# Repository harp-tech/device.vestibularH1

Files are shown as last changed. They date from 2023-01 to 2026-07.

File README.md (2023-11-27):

## Harp VestibularH1

This repository contains the device metadata, firmware and high-level interface to the VestibularH1 device. Below are simple getting started instructions for maintainers to create a new device using the automatic code generators.

### Device metadata

#### Prerequisites

1. Install [Visual Studio Code](https://code.visualstudio.com/)
2. Install the [YAML](https://marketplace.visualstudio.com/items?itemName=redhat.vscode-yaml) extension.

The `device.yml` file in the root of the project contains the VestibularH1 device metadata. A complete specification of device registers, including any bit masks, group masks, and payload specs needs to be provided for code generation to work.

### Generating interface and firmware

#### Prerequisites

1. Install [`dotnet`](https://dotnet.microsoft.com/)
2. Install `dotnet-t4`
```
dotnet tool install -g dotnet-t4
```

The `Generators` folder contains all text templates and project files required to generate both the firmware headers and the interface for the VestibularH1 device. To run the text templating engine just build the project inside this folder.

```
cd Generators
dotnet build
```

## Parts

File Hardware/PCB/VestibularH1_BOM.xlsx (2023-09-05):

VestibularVR H1-module v.1.1 BOM
Qty | Parts | Value | OEPS | MPN | Device | Package | Description
2 | R1, R5 | 0R | OEPS020001 | RC0402JR-070RL | R-US_R0402 | R0402@1 | RESISTOR, American symbol
14 | C3, C5, C7, C9, C12, C14, C15, C16, C17, C25, C26, C27, C28, C29 | 100nF | OEPS010004 | C1005X7R1H104K050BB | C-EUC0402K | C0402K | CAPACITOR, European symbol
4 | R4, R7, R18, R34 | 10k | OEPS020030 | CRCW040210K0FKED | R-US_R0402 | R0402@1 | RESISTOR, American symbol
3 | R3, R8, R9 | 1M | OEPS020026 | CRCW04021M00FKED | R-US_R0402 | R0402@1 | RESISTOR, American symbol
2 | LICK_0, LICK_1 | 1x3 case | OEPS070035 | 282834-3 | 22-23-2031 | 22-23-2031 | .100 (2.54mm) Center Header - 3 Pin"
2 | CAM_TRIGGERS, REWARD_VALVES | 1x4 case | OEPS070036 | 282834-4 | 22-23-2041 | 22-23-2041 | .100 (2.54mm) Center Header - 4 Pin"
2 | X1, X2 | 2x5 header | n.a. | 2x5 header | TSW-105-02-S-D | TSW-105-02-S-D | THROUGH-HOLE .025 SQ POST HEADER"
1 | R10 | 330R | OEPS020037 | RC0402FR-07330RL | R-EU_R0402 | R0402 | RESISTOR, European symbol
1 | C2 | 4.7nF | OEPS010001 | CC0402KRX7R8BB472 | C-EUC0402K | C0402K | CAPACITOR, European symbol
3 | C8, C10, C11 | 4.7uF | OEPS010018 | C1608X6S1C475K080AC | C-EUC0603 | C0603 | CAPACITOR, European symbol
2 | L1, L2 | 40R@100MHz | OEPS040003 | MI0805K400R-10 | R-EU_R0603 | R0603 | RESISTOR, European symbol
3 | C4, C6, C13 | 47pF | n.a. | 04025A470JAT2A | C-EUC0402K | C0402K | CAPACITOR, European symbol
1 | IC8 | ATXMEGA32A4U | OEPS080012 | ATXMEGA32A4U-AUR | XMEGA-A4_AT-XMEGA-XXA4-AUTQFP44 | TQFP44 | ATxMega a4 Serie
2 | D1, D4 | BAT54 | OEPS030003 | BAT54SLT1G | BAT54 | SOT23 | Schottky Diodes
2 | T1, T2 | DMG1012UW | OEPS060010 | DMG1012UW-7 | DMG1012UW-7 | SOT323 | N-CHANNEL ENHANCEMENT MODE MOSFET
2 | R2, R6 | DNI | DNI | DNI | R-US_R0402 | R0402@1 | RESISTOR, American symbol
1 | IC1 | FT232RL | OEPS080013 | FT232RL | FT232RL | SSOP28 | UART/FIFO IC
1 | STATE | GREEN_LED | OEPS030005 | LTST-C191KGKT | LEDCHIP-LED0603 | CHIP-LED0603 | LED
1 | IC3 | LP5907MFX-3.3 | OEPS080016 | LP5907MFX-3.3/NOPB | TLV700XX | TSOT23-5 | C REG LINEAR 3.3V 200MA SOT23-5
4 | IC2, IC4, IC5, IC9 | M74VHC1GT126DT1G | OEPS080017 | M74VHC1GT126DT1G | M74VHC1GT126DT1G | TSOP-5 | Single Buffer/Driver With Open-Drain Output
1 | X15 | Main_plug | OEPS070037 | 20.155MH/5-E | 90G-5 | 90G-5 | WEIDMUELLER CLAMP CONNECTOR
1 | OSC1 | OSCILLATOR | OEPS080018 | DSC1001CI5-032.0000 | OSCILLATOR | OSCILLATOR_3.2X2.5 | XTAL OSC TCXO 32.0000MHZ HCMOS
1 | SV2 | PINHD-2X3 | OEPS070015 | 609-3210-ND | PINHD-2X3 | 2X03 | PIN HEADER
1 | X3 | USB_MINI_B | OEPS070021 | UX60-MB-5S8 | USB_MINI_B | 240-0002-1 | CONN RCPT USB2.0 MINI B SMD R/A
1 | IC7 | USBLC6-2SC6 | OEPS030010 | USBLC6-2SC6 | USBLC6-2SC6 | SOT23-6L | TVS DIODE 5.25VWM 17VC SOT23-6
.off board
Qty | Value | Parts | OEPS | Device | MPN | Package | Description
1 | CONN RCPT 10POS IDC 28AWG | n.a. | OEPS070040 | - | 1658621-1 AKC10H-ND | 2x5 10mil pitch | IDC 2x5 10mil pitch
1 | PAA5100JE Near Optical Flow Camera SPI Breakout | n.a. | OEPS ?? | - | PAA5100JE | - | PAA5100JE-Q is PixArt Imaging's latest optical navigation chip
2 | Lick Sensor module v1.0 PCB | n.a. | OEPS ?? | - | Lick Sensor module v1.0 | - | Lick Sensor
1 | Pluggable Terminal Block, 3.5 mm, 5 Ways | n.a. | OEPS070038 | - | 20.1550M/5-E Farnell 2575218 | - | External Terminal Block
n | flat ribbon cable | n.a. | OEPS090003 | - | 3365/10-100SF | - | RIBON 10COND 28AWG GRAY 100FT 30.48metter

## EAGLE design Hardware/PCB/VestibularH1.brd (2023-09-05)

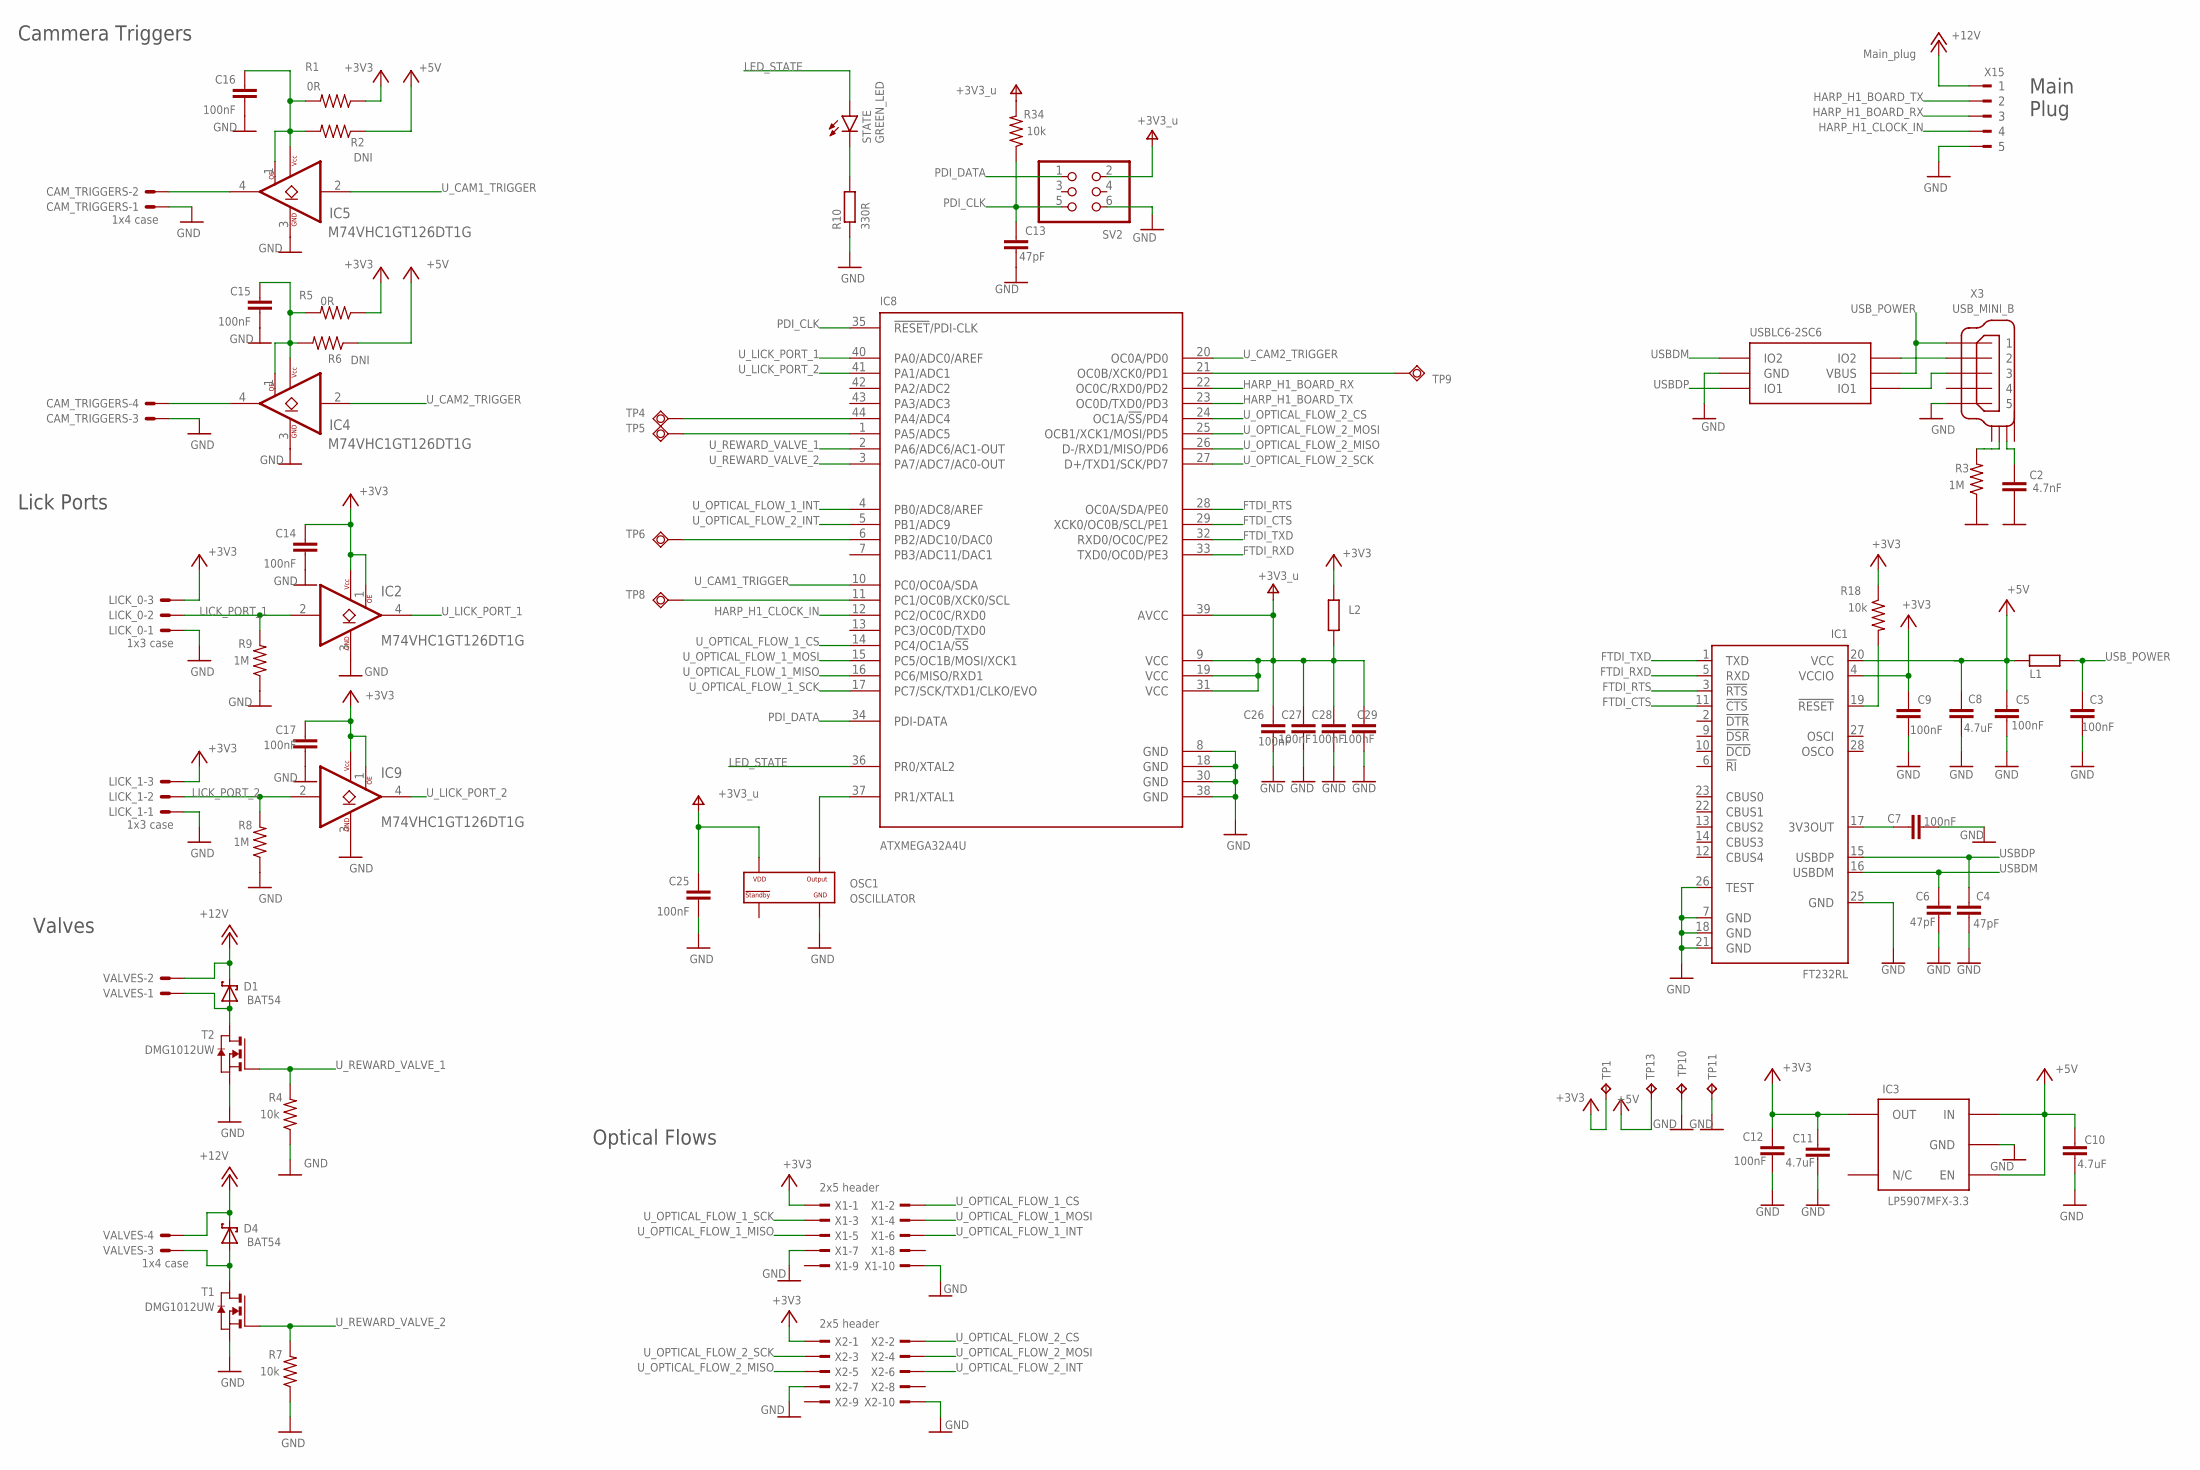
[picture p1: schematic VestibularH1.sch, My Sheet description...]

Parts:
C2: 4.7nF; C0402K; MPN CC0402KRX7R8BB472
C3, C5, C7, C9, C12, C14, C15, C16, C17, C25, C26, C27, C28, C29: 100nF; C0402K; MPN C1005X7R1H104K050BB; DIGIKEY_PN 445-5932-1-ND
C4, C6, C13: 47pF; C0402K; MPN 04025A470JAT2A
C8, C10: 4.7uF; C0603; MPN C1608X6S1C475K080AC
C11: 4.7uF; C0603K; MPN C1608X6S1C475K080AC
CAM_TRIGGERS: 1x4 case; 22-23-2041; MPN 282834-4
D1, D4: BAT54; SOT23; MPN BAT54SLT1G
IC1: FT232RL; SSOP28; MPN FT232RL
IC2, IC4, IC5, IC9: M74VHC1GT126DT1G; TSOP-5; MPN M74VHC1GT126DT1G; DIGIKEY_PN M74VHC1GT126DT1GOSDKR-ND
IC3: LP5907MFX-3.3; TSOT23-5; MPN LP5907MFX-3.3/NOPB
IC7: USBLC6-2SC6; SOT23-6L; MPN USBLC6-2SC6
IC8: ATXMEGA32A4U; TQFP44
L1, L2: 40R@100MHz; R0603; MPN MI0805K400R-10
LICK_0, LICK_1: 1x3 case; 22-23-2031; MPN 282834-3
OSC1: OSCILLATOR; OSCILLATOR_3.2X2.5; MPN DSC1001CI5-032.0000
R1, R5: 0R; R0402@1; MPN RC0402JR-070RL
R2, R6: DNI; R0402@1; MPN DNI
R3, R8, R9: 1M; R0402@1; MPN CRCW04021M00FKED; DIGIKEY_PN 541-1.00MLCT-ND
R4, R7, R18, R34: 10k; R0402@1; MPN CRCW040210K0FKED; DIGIKEY_PN 541-10.0KLDKR-ND
R10: 330R; R0402; MPN RC0402FR-07330RL
STATE: GREEN_LED; CHIP-LED0603; MPN LTST-C191KGKT
SV2: PINHD-2X3; 2X03; MPN 609-3210-ND
T1, T2: DMG1012UW; SOT323; MPN DMG1012UW-7
TP1, TP10, TP11, TP13: NO_COMPONENT; B1,27
TP4, TP5, TP6, TP8, TP9: NO_COMPONENT; TP11R
VALVES: 1x4 case; 22-23-2041; MPN 282834-4
X1, X2: 2x5 header; TSW-105-02-S-D; MPN 2x5 header
X3: USB_MINI_B; 240-0002-1; MPN UX60-MB-5S8
X15: Main_plug; 90G-5; MPN 20.155MH/5-E

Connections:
+3V3: C9.1, C11.1, C12.1, C14.1, C17.1, IC1.4 (VCCIO), IC2.1 (OE), IC2.5 (VCC), IC3.5 (OUT), IC9.1 (OE), IC9.5 (VCC), L2.2, LICK_0.3, LICK_1.3, R1.1, R5.1, R18.1, TP1.TP, X1.1, X2.1
+3V3_U: C25.1, C26.1, C27.1, C28.1, C29.1, IC8.9 (VCC), IC8.19 (VCC), IC8.31 (VCC), IC8.39 (AVCC), L2.1, OSC1.P$4 (VDD), R34.2, SV2.2
+5V: C5.1, C8.1, C10.1, IC1.20 (VCC), IC3.1 (IN), IC3.3 (EN), L1.1, R2.1, R6.1, TP13.TP
+12V: D1.3 (C), D4.3 (C), VALVES.2, VALVES.4, X15.1
FTDI_CTS: IC1.11 (!CTS), IC8.29 (XCK0/OC0B/SCL/PE1)
FTDI_RTS: IC1.3 (!RTS), IC8.28 (OC0A/SDA/PE0)
FTDI_RXD: IC1.5 (RXD), IC8.33 (TXD0/OC0D/PE3)
FTDI_TXD: IC1.1 (TXD), IC8.32 (RXD0/OC0C/PE2)
GND: C2.2, C3.2, C4.2, C5.2, C6.2, C7.2, C8.2, C9.2, C10.2, C11.2, C12.2, C13.2, C14.2, C15.2, C16.2, C17.2, C25.2, C26.2, C27.2, C28.2, C29.2, CAM_TRIGGERS.1, CAM_TRIGGERS.3, IC1.7 (GND), IC1.18 (GND), IC1.21 (GND), IC1.25 (GND), IC1.26 (TEST), IC2.3 (GND), IC3.2 (GND), IC4.3 (GND), IC5.3 (GND), IC7.P$2 (GND), IC8.8 (GND), IC8.18 (GND), IC8.30 (GND), IC8.38 (GND), IC9.3 (GND), LICK_0.1, LICK_1.1, OSC1.P$2 (GND), R3.1, R4.1, R7.1, R8.1, R9.1, R10.1, SV2.6, T1.2 (S), T2.2 (S), TP10.TP, TP11.TP, X1.7, X1.10, X2.7, X2.10, X3.P$5 (5), X15.5
HARP_H1_BOARD_RX: IC8.22 (OC0C/RXD0/PD2), X15.3
HARP_H1_BOARD_TX: IC8.23 (OC0D/TXD0/PD3), X15.2
HARP_H1_CLOCK_IN: IC8.12 (PC2/OC0C/RXD0), X15.4
LED_STATE: IC8.36 (PR0/XTAL2), STATE.A
LICK_PORT_1: IC2.2 (A), LICK_0.2, R9.2
LICK_PORT_2: IC9.2 (A), LICK_1.2, R8.2
unnamed: R3.2, X3.SHIELD_2
unnamed: IC7.P$4 (IO2), X3.P$2 (2)
unnamed: IC7.P$6 (IO1), X3.P$3 (3)
unnamed: CAM_TRIGGERS.4, IC4.4 (Y)
unnamed: C16.1, IC5.1 (OE), IC5.5 (VCC), R1.2, R2.2
unnamed: D4.1 (A), T1.3 (D), VALVES.3
unnamed: CAM_TRIGGERS.2, IC5.4 (Y)
unnamed: R10.2, STATE.C
unnamed: IC8.44 (PA4/ADC4), TP4.TP
unnamed: IC8.1 (PA5/ADC5), TP5.TP
unnamed: IC8.6 (PB2/ADC10/DAC0), TP6.TP
unnamed: C15.1, IC4.1 (OE), IC4.5 (VCC), R5.2, R6.2
unnamed: C2.1, X3.SHIELD_3
unnamed: IC8.11 (PC1/OC0B/XCK0/SCL), TP8.TP
unnamed: IC8.21 (OC0B/XCK0/PD1), TP9.TP
unnamed: C7.1, IC1.17 (3V3OUT)
unnamed: D1.1 (A), T2.3 (D), VALVES.1
unnamed: IC1.19 (!RESET), R18.2
OSC2: IC8.37 (PR1/XTAL1), OSC1.P$3 (OUTPUT)
PDI_CLK: C13.1, IC8.35 (!RESET!/PDI-CLK), R34.1, SV2.5
PDI_DATA: IC8.34 (PDI-DATA), SV2.1
USBDM: C6.1, IC1.16 (USBDM), IC7.P$3 (IO2)
USBDP: C4.1, IC1.15 (USBDP), IC7.P$1 (IO1)
USB_POWER: C3.1, IC7.P$5 (VBUS), L1.2, X3.P$1 (1)
U_CAM1_TRIGGER: IC5.2 (A), IC8.10 (PC0/OC0A/SDA)
U_CAM2_TRIGGER: IC4.2 (A), IC8.20 (OC0A/PD0)
U_LICK_PORT_1: IC2.4 (Y), IC8.40 (PA0/ADC0/AREF)
U_LICK_PORT_2: IC8.41 (PA1/ADC1), IC9.4 (Y)
U_OPTICAL_FLOW_1_CS: IC8.14 (PC4/OC1A/!SS), X1.2
U_OPTICAL_FLOW_1_INT: IC8.4 (PB0/ADC8/AREF), X1.6
U_OPTICAL_FLOW_1_MISO: IC8.16 (PC6/MISO/RXD1), X1.5
U_OPTICAL_FLOW_1_MOSI: IC8.15 (PC5/OC1B/MOSI/XCK1), X1.4
U_OPTICAL_FLOW_1_SCK: IC8.17 (PC7/SCK/TXD1/CLKO/EVO), X1.3
U_OPTICAL_FLOW_2_CS: IC8.24 (OC1A/!SS!/PD4), X2.2
U_OPTICAL_FLOW_2_INT: IC8.5 (PB1/ADC9), X2.6
U_OPTICAL_FLOW_2_MISO: IC8.26 (D-/RXD1/MISO/PD6), X2.5
U_OPTICAL_FLOW_2_MOSI: IC8.25 (OCB1/XCK1/MOSI/PD5), X2.4
U_OPTICAL_FLOW_2_SCK: IC8.27 (D+/TXD1/SCK/PD7), X2.3
U_REWARD_VALVE_1: IC8.2 (PA6/ADC6/AC1-OUT), R4.2, T2.1 (G)
U_REWARD_VALVE_2: IC8.3 (PA7/ADC7/AC0-OUT), R7.2, T1.1 (G)

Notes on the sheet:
Valves
Lick Ports
Cammera Triggers
Main Plug
Optical Flows

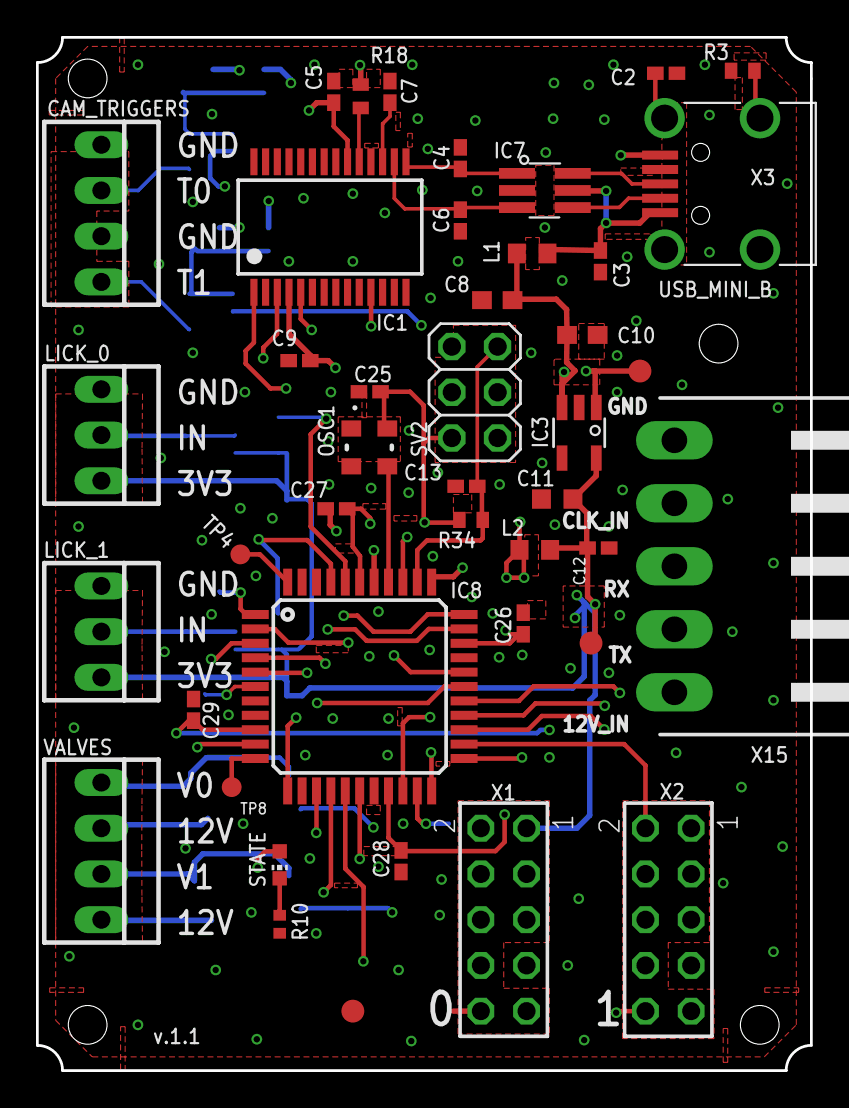
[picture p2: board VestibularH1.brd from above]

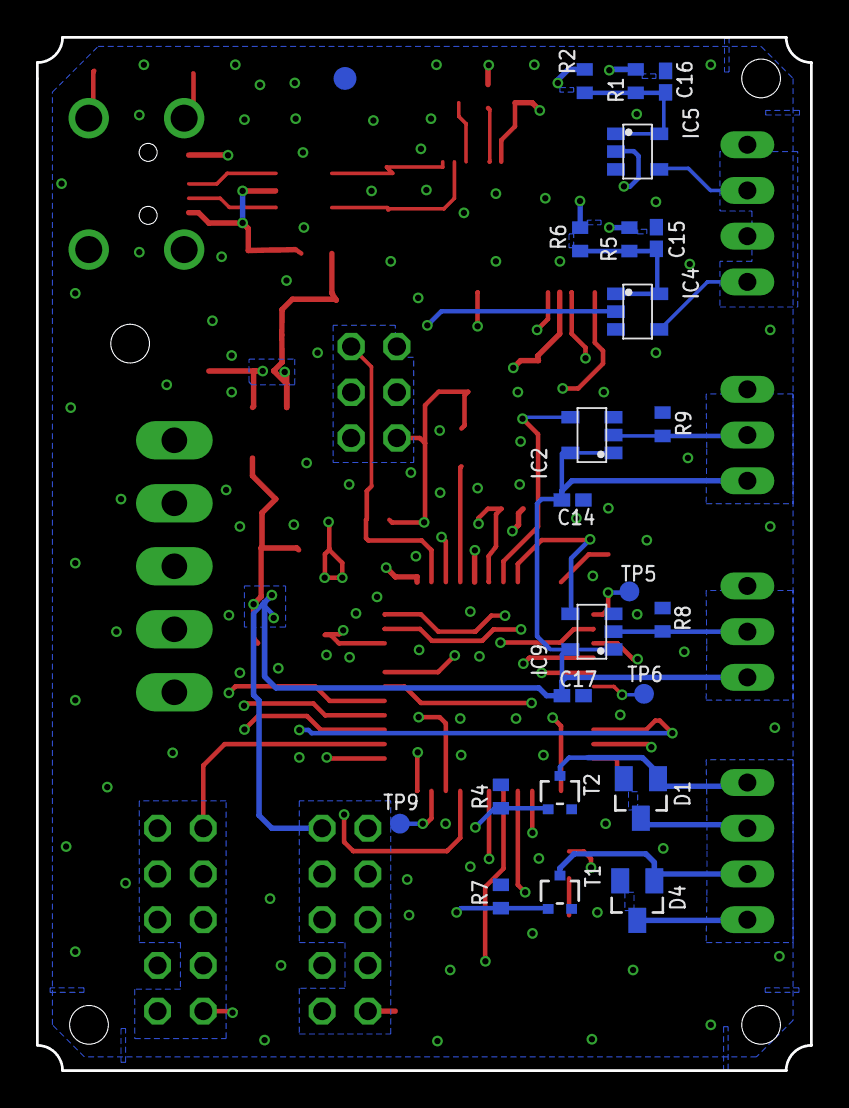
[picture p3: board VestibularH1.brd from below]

Board: 4 copper layers, 43.0 x 57.4 mm, 67 parts (24 on the bottom side), 55 nets.

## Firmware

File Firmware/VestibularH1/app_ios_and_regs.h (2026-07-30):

#ifndef _APP_IOS_AND_REGS_H_
#define _APP_IOS_AND_REGS_H_
#include "cpu.h"

void init_ios(void);
/************************************************************************/
/* Definition of input pins                                             */
/************************************************************************/
// LICK0                  Description: Input for the Lick 0
// LICK1                  Description: Input for the Lick 1

#define read_LICK0 read_io(PORTA, 0)            // LICK0
#define read_LICK1 read_io(PORTA, 1)            // LICK1

/************************************************************************/
/* Definition of output pins                                            */
/************************************************************************/
// LED_STATE              Description: Power's LED
// CAM0_TRIGGER           Description: Trigger for cammera 0 (T0)
// CAM1_TRIGGER           Description: Trigger for cammera 1 (T1)
// VALVE0                 Description: Controls the transitor of Valve 0
// VALVE1                 Description: Controls the transitor of Valve 1
// FLOW0_CS               Description: Flow meter SPI line CS
// FLOW0_MOSI             Description: Flow meter SPI line MOSI
// FLOW0_SCK              Description: Flow meter SPI line SCK
// FLOW1_CS               Description: Flow meter SPI line CS
// FLOW1_MOSI             Description: Flow meter SPI line MOSI
// FLOW1_SCK              Description: Flow meter SPI line SCK

/* LED_STATE */
#define set_LED_STATE set_io(PORTR, 0)
#define clr_LED_STATE clear_io(PORTR, 0)
#define tgl_LED_STATE toggle_io(PORTR, 0)
#define read_LED_STATE read_io(PORTR, 0)

/* CAM0_TRIGGER */
#define set_CAM0_TRIGGER set_io(PORTC, 0)
#define clr_CAM0_TRIGGER clear_io(PORTC, 0)
#define tgl_CAM0_TRIGGER toggle_io(PORTC, 0)
#define read_CAM0_TRIGGER read_io(PORTC, 0)

/* CAM1_TRIGGER */
#define set_CAM1_TRIGGER set_io(PORTD, 0)
#define clr_CAM1_TRIGGER clear_io(PORTD, 0)
#define tgl_CAM1_TRIGGER toggle_io(PORTD, 0)
#define read_CAM1_TRIGGER read_io(PORTD, 0)

/* VALVE0 */
#define set_VALVE0 set_io(PORTA, 6)
#define clr_VALVE0 clear_io(PORTA, 6)
#define tgl_VALVE0 toggle_io(PORTA, 6)
#define read_VALVE0 read_io(PORTA, 6)

/* VALVE1 */
#define set_VALVE1 set_io(PORTA, 7)
#define clr_VALVE1 clear_io(PORTA, 7)
#define tgl_VALVE1 toggle_io(PORTA, 7)
#define read_VALVE1 read_io(PORTA, 7)

/* FLOW0_CS */
#define set_FLOW0_CS set_io(PORTC, 4)
#define clr_FLOW0_CS clear_io(PORTC, 4)
#define tgl_FLOW0_CS toggle_io(PORTC, 4)
#define read_FLOW0_CS read_io(PORTC, 4)

/* FLOW0_MOSI */
#define set_FLOW0_MOSI set_io(PORTC, 5)
#define clr_FLOW0_MOSI clear_io(PORTC, 5)
#define tgl_FLOW0_MOSI toggle_io(PORTC, 5)
#define read_FLOW0_MOSI read_io(PORTC, 5)

/* FLOW0_SCK */
#define set_FLOW0_SCK set_io(PORTC, 7)
#define clr_FLOW0_SCK clear_io(PORTC, 7)
#define tgl_FLOW0_SCK toggle_io(PORTC, 7)
#define read_FLOW0_SCK read_io(PORTC, 7)

/* FLOW1_CS */
#define set_FLOW1_CS set_io(PORTD, 4)
#define clr_FLOW1_CS clear_io(PORTD, 4)
#define tgl_FLOW1_CS toggle_io(PORTD, 4)
#define read_FLOW1_CS read_io(PORTD, 4)

/* FLOW1_MOSI */
#define set_FLOW1_MOSI set_io(PORTD, 5)
#define clr_FLOW1_MOSI clear_io(PORTD, 5)
#define tgl_FLOW1_MOSI toggle_io(PORTD, 5)
#define read_FLOW1_MOSI read_io(PORTD, 5)

/* FLOW1_SCK */
#define set_FLOW1_SCK set_io(PORTD, 7)
#define clr_FLOW1_SCK clear_io(PORTD, 7)
#define tgl_FLOW1_SCK toggle_io(PORTD, 7)
#define read_FLOW1_SCK read_io(PORTD, 7)


/************************************************************************/
/* Registers' structure                                                 */
/************************************************************************/
typedef struct
{
	uint8_t REG_CAM0_EVENT;
	uint8_t REG_CAM1_EVENT;
	uint16_t REG_CAM0_TRIGGER_FREQUENCY;
	uint16_t REG_CAM0_TRIGGER_DURATION_US;
	uint16_t REG_CAM1_TRIGGER_FREQUENCY;
	uint16_t REG_CAM1_TRIGGER_DURATION_US;
	uint8_t REG_START_AND_STOP;
	uint8_t REG_IN_STATE;
	uint8_t REG_VALVE0_PULSE;
	uint8_t REG_VALVE1_PULSE;
	uint8_t REG_OUT_SET;
	uint8_t REG_OUT_CLEAR;
	uint8_t REG_OUT_TOGGLE;
	uint8_t REG_OUT_WRITE;
	int16_t REG_REG_OPTICAL_TRACKING_READ[6];
	uint8_t REG_PRODUCT_ID_PORT0;
	uint8_t REG_PRODUCT_ID_PORT1;
	uint16_t REG_CPI;
	uint8_t REG_MCA_SIGNAL_SELECT;
	float REG_MCA_SIGNAL_GAIN;
	float REG_MCA_ZERO_THRESHOLD;
	uint16_t REG_MCA_MAX_PULSE_INTERVAL;
	uint16_t REG_MCA_MIN_PULSE_INTERVAL;
} AppRegs;

/************************************************************************/
/* Registers' address                                                   */
/************************************************************************/
/* Registers */
#define ADD_REG_CAM0_EVENT                  32 // U8     
#define ADD_REG_CAM1_EVENT                  33 // U8     
#define ADD_REG_CAM0_TRIGGER_FREQUENCY      34 // U16    Sets the trigger frequency for camera 0 between 1 and 1000
#define ADD_REG_CAM0_TRIGGER_DURATION_US    35 // U16    Sets the duration of the trigger pulse (minimum is 100) for camera 0
#define ADD_REG_CAM1_TRIGGER_FREQUENCY      36 // U16    Sets the trigger frequency for camera 1 between 1 and 1000
#define ADD_REG_CAM1_TRIGGER_DURATION_US    37 // U16    Sets the duration of the trigger pulse (minimum is 100) for camera 1
#define ADD_REG_START_AND_STOP              38 // U8     Starts or stops the cameras immediately
#define ADD_REG_IN_STATE                    39 // U8     Contains the state of the lick ports
#define ADD_REG_VALVE0_PULSE                40 // U8     Configures the valve 0 open time in milliseconds
#define ADD_REG_VALVE1_PULSE                41 // U8     Configures the valve 1 open time in milliseconds
#define ADD_REG_OUT_SET                     42 // U8     Bitmask to set the available outputs
#define ADD_REG_OUT_CLEAR                   43 // U8     Bitmask to clear the digital ouputs
#define ADD_REG_OUT_TOGGLE                  44 // U8     Bitmask to toggle the digital ouputs
#define ADD_REG_OUT_WRITE                   45 // U8     Bitmask to write the digital ouputs
#define ADD_REG_REG_OPTICAL_TRACKING_READ   46 // I16    
#define ADD_REG_PRODUCT_ID_PORT0            47 // U8     Contains de flow meter ID connected to Port 0
#define ADD_REG_PRODUCT_ID_PORT1            48 // U8     Contains de flow meter ID connected to Port 1
#define ADD_REG_CPI                         49 // U16    Configures the counts per inch for both channels (PMW3360 with prodID=66 only). Maximum is 12000.
#define ADD_REG_MCA_SIGNAL_SELECT           50 // U8     Select which sensor and axis will be used as the input signal for the motion control algorithm (MCA)
#define ADD_REG_MCA_SIGNAL_GAIN             51 // FLOAT  Gain to be applied to the input signal
#define ADD_REG_MCA_ZERO_THRESHOLD          52 // FLOAT  Specifies deadband for conversion from speed delta to motor's immediate pulses in us
#define ADD_REG_MCA_MAX_PULSE_INTERVAL      53 // U16    Specifies the maximum of the motor's pulse interval in us
#define ADD_REG_MCA_MIN_PULSE_INTERVAL      54 // U16    Specifies the minimum of the motor's pulse interval in us

/************************************************************************/
/* PWM Generator registers' memory limits                               */
/*                                                                      */
/* DON'T change the APP_REGS_ADD_MIN value !!!                          */
/* DON'T change these names !!!                                         */
/************************************************************************/
/* Memory limits */
#define APP_REGS_ADD_MIN                    0x20
#define APP_REGS_ADD_MAX                    0x36
#define APP_NBYTES_OF_REG_BANK              47

/************************************************************************/
/* Registers' bits                                                      */
/************************************************************************/
#define B_TRIGGER                          (1<<0)       // A trigger was sent to camera
#define B_START_CAM0                       (1<<0)       // 
#define B_START_CAM1                       (1<<1)       // 
#define B_STOP_CAM0                        (1<<2)       // 
#define B_STOP_CAM1                        (1<<3)       // 
#define B_LICK0                            (1<<0)       // 
#define B_LICK1                            (1<<1)       // 
#define B_LICK0_CHANGED                    (1<<4)       // 
#define B_LICK1_CHANGED                    (1<<5)       // 
#define B_TRIGGER_CAM0                     (1<<0)       // 
#define B_TRIGGER_CAM1                     (1<<1)       // 
#define B_VALVE0                           (1<<2)       // 
#define B_VALVE1                           (1<<3)       // 
#define B_PULSE_VALVE0                     (1<<4)       // 
#define B_PULSE_VALVE1                     (1<<5)       // 
#define GM_MCA_CONFIG                      7            // 
#define MSK_MCA_OFF                        0            // 
#define MSK_MCA_DELTAX0                    1            // 
#define MSK_MCA_DELTAY0                    2            // 
#define MSK_MCA_DELTAX1                    3            // 
#define MSK_MCA_DELTAY1                    4            // 

#endif /* _APP_REGS_H_ */

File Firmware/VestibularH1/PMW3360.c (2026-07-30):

#include "PMW3360.h"
#include "spi.h"
#include "app_ios_and_regs.h"
#include <avr/pgmspace.h>

#define F_CPU 32000000
#include <util/delay.h>

uint8_t productID;
uint8_t invProductID;
uint8_t sromID;

extern uint8_t prodIdPort0;
extern uint8_t prodIdPort1;

bool optical_tracking_initialize_pwm3360_0(void)
{
	/* Shutdown */
	optical_tracking_write_register_pmw3360_0(REG_Shutdown, 0xB6);
	_delay_ms(300);
	
	/* Restart SPI */
	spi_start_flow0();
	_delay_us(40);
	spi_stop_flow0();
	_delay_us(40);
	
	/* Power up and reset */
	optical_tracking_write_register_pmw3360_0(REG_Power_Up_Reset, 0x5A);	// Reset
	_delay_ms(100);
	
	/* Check if the right IC is present */
	uint8_t prodID = check_signatures_pmw3360_0(false);
	if (prodID == 0)
		return false;
	else
		prodIdPort0 = prodID;
	
	/* Read the data registers */
	optical_tracking_read_register_pwm3360_0(REG_Motion);
	optical_tracking_read_register_pwm3360_0(REG_Delta_X_L);
	optical_tracking_read_register_pwm3360_0(REG_Delta_X_H);
	optical_tracking_read_register_pwm3360_0(REG_Delta_Y_L);
	optical_tracking_read_register_pwm3360_0(REG_Delta_Y_H);
	
	/* Upload firmware */
	if (prodID == 0x42)
		upload_the_firmware_pmw3360_0();
	
	/* Check all signatures including SROM */
	if (prodID == 0x42)
		if (check_signatures_pmw3360_0(true) == false)
			return false;
	
	_delay_ms(10);
	
	return true;
}

bool optical_tracking_initialize_pwm3360_1(void)
{
	/* Shutdown */
	optical_tracking_write_register_pmw3360_1(REG_Shutdown, 0xB6);
	_delay_ms(300);
	
	/* Restart SPI */
	spi_start_flow1();
	_delay_us(40);
	spi_stop_flow1();
	_delay_us(40);
	
	/* Power up and reset */
	optical_tracking_write_register_pmw3360_1(REG_Power_Up_Reset, 0x5A);	// Reset
	_delay_ms(100);
	
	/* Check if the right IC is present */
	uint8_t prodID = check_signatures_pmw3360_1(false);
	if (prodID == 0)
		return false;
	else
		prodIdPort1 = prodID;
	
	/* Read the data registers */
	optical_tracking_read_register_pwm3360_1(REG_Motion);
	optical_tracking_read_register_pwm3360_1(REG_Delta_X_L);
	optical_tracking_read_register_pwm3360_1(REG_Delta_X_H);
	optical_tracking_read_register_pwm3360_1(REG_Delta_Y_L);
	optical_tracking_read_register_pwm3360_1(REG_Delta_Y_H);
	
	/* Upload firmware */
	if (prodID == 0x42)
	upload_the_firmware_pmw3360_1();
	
	/* Check all signatures including SROM */
	if (prodID == 0x42)
	if (check_signatures_pmw3360_1(true) == false)
	return false;
	
	_delay_ms(10);
	
	return true;
}


uint8_t check_signatures_pmw3360_0(bool check_srom)
{
	uint8_t productID = optical_tracking_read_register_pwm3360_0(REG_Product_ID);
	uint8_t invProductID = optical_tracking_read_register_pwm3360_0(REG_Inverse_Product_ID);
	uint8_t sromID = optical_tracking_read_register_pwm3360_0(REG_SROM_ID);
	
	/* Check product ID */
	if (productID != 0x42 && productID != 0x47)
	return false;
	
	if (productID == 0x42)
	if (invProductID != 0xBD)
	return 0;
	
	if (productID == 0x47)
	if (invProductID != 0xB8)
	return 0;
	
	/* Read the SROM_ID register to verify the firmware ID */
	if (check_srom)
	if (sromID != 0x04)
	return 0;
	
	return productID;
}

uint8_t check_signatures_pmw3360_1(bool check_srom)
{
	uint8_t productID = optical_tracking_read_register_pwm3360_1(REG_Product_ID);
	uint8_t invProductID = optical_tracking_read_register_pwm3360_1(REG_Inverse_Product_ID);
	uint8_t sromID = optical_tracking_read_register_pwm3360_1(REG_SROM_ID);
	
	/* Check product ID */
	if (productID != 0x42 && productID != 0x47)
	return false;
	
	if (productID == 0x42)
	if (invProductID != 0xBD)
	return 0;
	
	if (productID == 0x47)
	if (invProductID != 0xB8)
	return 0;
	
	/* Read the SROM_ID register to verify the firmware ID */
	if (check_srom)
	if (sromID != 0x04)
	return 0;
	
	return productID;
}
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

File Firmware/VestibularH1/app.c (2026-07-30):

#include "hwbp_core.h"
#include "hwbp_core_regs.h"
#include "hwbp_core_types.h"

#include "app.h"
#include "app_funcs.h"
#include "app_ios_and_regs.h"

#include "spi.h"
#include "PAA5100JE.h"
#include "PMW3360.h"

/************************************************************************/
/* Declare application registers                                        */
/************************************************************************/
extern AppRegs app_regs;
extern uint8_t app_regs_type[];
extern uint16_t app_regs_n_elements[];
extern uint8_t *app_regs_pointer[];
extern void (*app_func_rd_pointer[])(void);
extern bool (*app_func_wr_pointer[])(void*);

/************************************************************************/
/* Initialize app                                                       */
/************************************************************************/
static const uint8_t default_device_name[] = "VestibularH1";

void hwbp_app_initialize(void)
{
    /* Start core */
	core_func_start_core_V2(
		WHO_AM_I,
		MAJOR_HW_VERSION, MINOR_HW_VERSION, PATCH_HW_VERSION,
		MAJOR_FW_VERSION, MINOR_FW_VERSION, PATCH_FW_VERSION,
		(uint8_t*)(&app_regs),
		APP_NBYTES_OF_REG_BANK,
		APP_REGS_ADD_MAX - APP_REGS_ADD_MIN + 1,
		default_device_name,
		true,	// The device is able to repeat the harp timestamp clock
		false,	// The device is _not_ able to generate the harp timestamp clock
		0		// Default timestamp offset
	);
}

/************************************************************************/
/* Handle if a catastrophic error occur                                 */
/************************************************************************/
void core_callback_catastrophic_error_detected(void)
{
	
}
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

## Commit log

2022-10-06 VestibularVR H1-module v1.0: PCB design update
    VestibularVR H1-module v1.0 design
    - Eagle migration
    - start buffering & PCB integration & size
    - plugs & headers not selected yet; but on schm already
    [VestibularVR H1-module v1.0.brd, VestibularVR H1-module v1.0.sch]
2022-10-09 pcb v1.0 developed
    [VestibularVR H1-module v1.0.brd, VestibularVR H1-module v1.0.sch]
2022-10-13 proceeding design VestibularVR H1
    - Eagle version changed back to v.8.3.1
    - proceeding design VestibularVR H1-module v1.0
    - added Lick Sensor module v1.0
    [VestibularVR H1-module v1.0.brd, VestibularVR H1-module v1.0.sch]
2022-10-14 update on VestibularVR & LickSensor
    - returned to Eagle 9.6.2
    - projects reviewed with Filipe
    - LickSensor board with reviews already made
    - VestibularVR board starting implementing reviews
    [VestibularVR H1-module v1.0.brd, VestibularVR H1-module v1.0.sch]
2022-10-31 VestibularVR H1-module v1.0 - revisions made with Filipe updated
    Revisions made:
    - added missing decoupler caps
    - considered components on top & bottom side
    - review pinout on micro
    Next steps:
    - final mechanical integration
    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
    [VestibularVR H1-module v1.0.brd, VestibularVR H1-module v1.0.sch]
2022-11-03 . schm design reviewed 2nd time with Filipe . pcb design already started; not finished
    [VestibularVR H1-module v1.0.brd, VestibularVR H1-module v1.0.sch]
2022-11-04 same as last commit: . procceding pcb design
    [VestibularVR H1-module v1.0.brd, VestibularVR H1-module v1.0.sch]
2022-11-04 . pcb design; not finnished
    [VestibularVR H1-module v1.0.brd, VestibularVR H1-module v1.0.sch]
2022-11-07 . 1st stage pcb design finnalized . missing: . put couple test poitns . move mechanical hole from one to other side usb plug . Filipe going to do a revision
    [VestibularVR H1-module v1.0.brd, VestibularVR H1-module v1.0.sch]
2022-11-07 v.1.0 pcb design as finished; still missing to hear about it from Filipe
    . David's pcb v.1.0 design as finished
    - mechanical holes final tuning
    - main labels final design
    . still missing to hear about it from Filipe
    . next step - building BOM
    [VestibularVR H1-module v1.0.brd, VestibularVR H1-module v1.0.sch]
2022-11-09 final versions committed & CAM data
    VestibularVR H1-module v1.0
    &
    Lick Sensor module v1.0
    final versions committed !!!
    .created CAM data for both boards
    [VestibularVR H1-module v1.0.brd, VestibularVR H1-module v1.0.sch]
2022-11-09 tunings on last versions
    tunings on last versions:
    - labels size & positions
    - VestibularVR H1 module get 1mm more height
    [VestibularVR H1-module v1.0.brd, VestibularVR H1-module v1.0.sch]
2022-11-14 BOMs building
    . BOMs building:
    - for both projects - Lick Sensor Module v1.0 & VestibularVR H1 Module v1.0
    - schm files modified (components parameters updated)
    . Removed old Auxiliary Designs
    [VestibularVR H1-module v1.0 BOM.xlsx, VestibularVR H1-module v1.0.brd, VestibularVR H1-module v1.0.sch]
2022-11-21 BOM files
    BOM files
    - Lick sensor module v1.0 BOM; NOT FINAL
    VESTIBULARVR H1 v.1.0: added schm notes
    - VESTIBULARVR H1 v.1.0 BOM; NOT FINAL
    [VestibularVR H1-module v1.0 BOM.xlsx, VestibularVR H1-module v1.0.brd, VestibularVR H1-module v1.0.sch]
2022-11-21 BOM being updated
    BOM being updated
    not yet finished
    [VestibularVR H1-module v1.0 BOM.xlsx, VestibularVR H1-module v1.0.brd, VestibularVR H1-module v1.0.sch]
2022-11-22 BOMs & start Harp Motor device H2-module v1.0
    . almost final BOMs versions for VestibularVR H1-module v1.0 & Lick Sensor module v1.0
    . start of new project Harp Motor device H2-module v1.0
    [VestibularVR H1-module v1.0 BOM.xlsx, VestibularVR H1-module v1.0.brd, VestibularVR H1-module v1.0.sch]
2022-11-25 VestibularVR H1 module & Lick Sensor module v1.0 FINAL BOMs
    final BOM versions
    . VestibularVR H1 module
    . Lick Sensor module v1.0
    [VestibularVR H1-module v1.0 BOM.xlsx, VestibularVR H1-module v1.0.brd, VestibularVR H1-module v1.0.sch]
2022-12-05 VestibularVR H1BOM updates & Lick Sensor step on
    - VestibularVR H1
    . component ref updated
    . BOM file updated
    - Lick Sensor module v1.0
    . still only on schematic design
    [VestibularVR H1-module v1.0 BOM.xlsx, VestibularVR H1-module v1.0.brd, VestibularVR H1-module v1.0.sch]
2023-01-06 >> VestibularVR H1-module v1.0: corrected part numbers
    >> VestibularVR H1-module v1.0
    - notes added on schematic
    . buffers with wrong pn - corrected OEPS code; still wrong buffers' symbol
    generated new BOM with corrected pn
    [VestibularVR H1-module v1.0 BOM.xlsx, VestibularVR H1-module v1.0.brd, VestibularVR H1-module v1.0.sch]
2023-01-15 Reorganize repository to match standard template
    [VestibularVR H1-module v1.0 BOM.xlsx, VestibularVR H1-module v1.0.brd, VestibularVR H1-module v1.0.sch]
2023-01-15 Initial commit of firmware files.
    Already implements the valves, the cameras, and the lick inputs.
    [registers.xls]
2023-01-15 Added optical flow reading on both ports.
2023-01-15 Added control of both cameras.
2023-01-15 Minor corrections on descriptions.
    [registers.xls]
2023-01-16 Refactor firmware references to match device name
    [registers.xls]
2023-02-13 Fix device interface specification
2023-04-21 Update source generators and device metadata
2023-09-05 Replaced files with version 1.1.
    [VestibularH1.brd, VestibularH1.sch]
2023-09-05 Replaced BOM with version 1.1.
    [VestibularH1_BOM.xlsx, VestibularVR H1-module v1.0 BOM.xlsx]
2023-10-14 Increased delay after reset for power up time.
2023-10-14 Added SPI mode 3 and initial flow meter verification.
2023-10-14 Fixed used flow meter selection.
2023-10-14 Major update.
    Includes the entire code for the flow meter PMW3360.
2023-10-14 Created he new registers.
    Registers list:
    ADD_REG_PRODUCT_ID_PORT0 47 U8
    ADD_REG_PRODUCT_ID_PORT1 48 U8
    ADD_REG_CPI 49 U16
    [registers.xls]
2023-10-14 Created functionality to read the flow meter ID.
2023-10-14 Added limit to register CPI.
    [registers.xls]
2024-06-27 Added the new registers.
    [registers.xls]
2024-06-27 Implemented algorithm and added boundaries.
    [registers.xls]
2024-06-28 Implemented serial TX.
    [registers.xls]
